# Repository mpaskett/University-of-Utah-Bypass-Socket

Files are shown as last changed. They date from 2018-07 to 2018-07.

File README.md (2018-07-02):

# University-of-Utah-Bypass-Socket
The University of Utah’s bypass socket is a powerful tool enabling non-amputees to perform functional tasks with upper-limb prosthetic devices. Utilizing modular 3D-printed components, the bypass socket can be easily adapted to virtually any prosthetic device. We hope the bypass socket can become a useful resource to researchers, clinicians, educators, and insurers in the upper-limb prosthetics field. 

Find the necessary instructions and files for making your own bypass socket here.

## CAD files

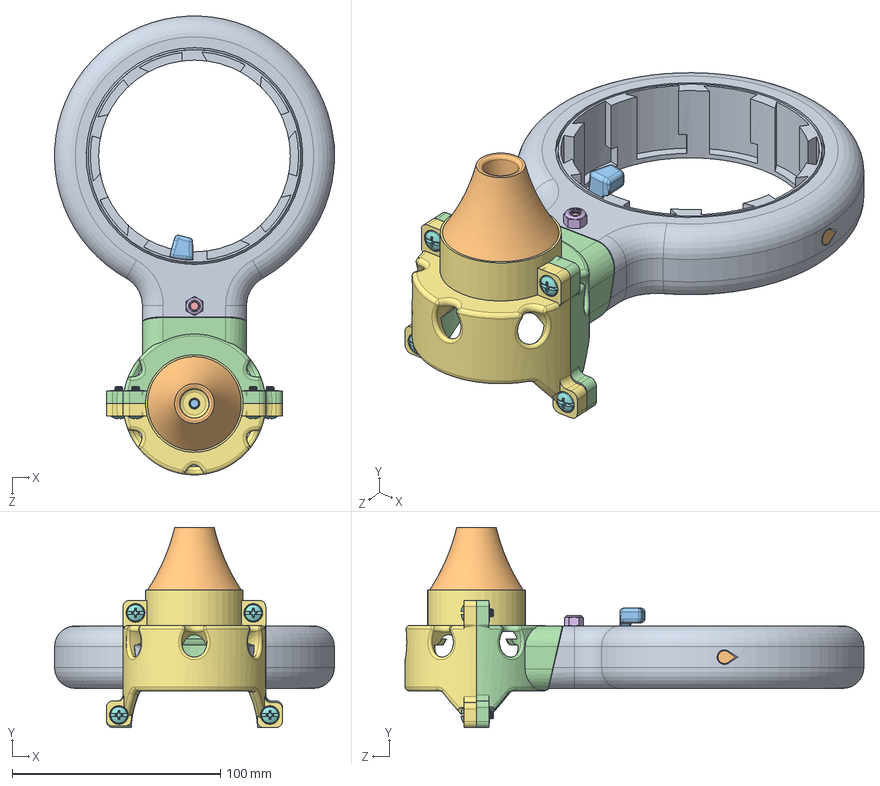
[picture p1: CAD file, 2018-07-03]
Assemblies/Wrist Assembly.SLDASM
134.4 x 96.0 x 220.2 mm
Bypass Bearing Keyfit
Bypass Bearing Insert
Wrist Locker
DEKA Bypass Adapter Nut Side
M5 Hex Screw Wrist - 91280A238
Nylon Insert Locknut - 90576A104
DEKA Bypass Adapter Bolt Side
8-32 Phillips Screw Wrist - 90604A194 x 4
8-32 Steel Hex Nut Wrist - 90480A009 x 4
Bypass Adapter Proximal Support
M5 Hex Head Screw Wrist - 91280A242

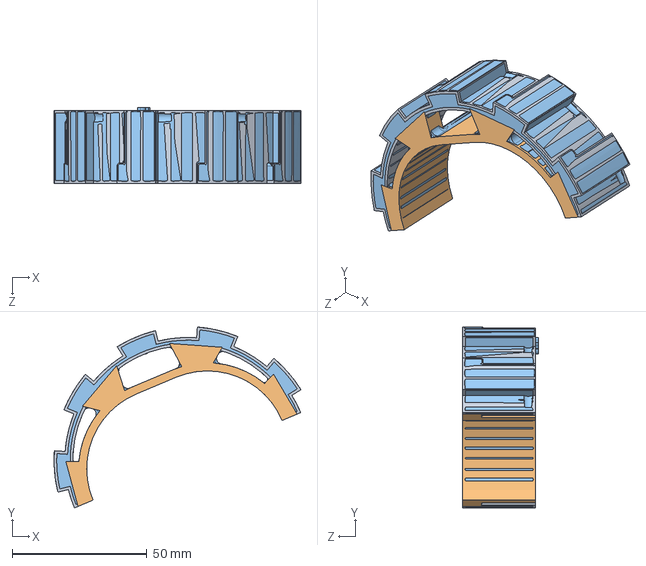
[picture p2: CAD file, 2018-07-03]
Parts/3D Prints/Normal Support/Wrist Attachment Small.SLDASM
91.5 x 67.0 x 28.0 mm

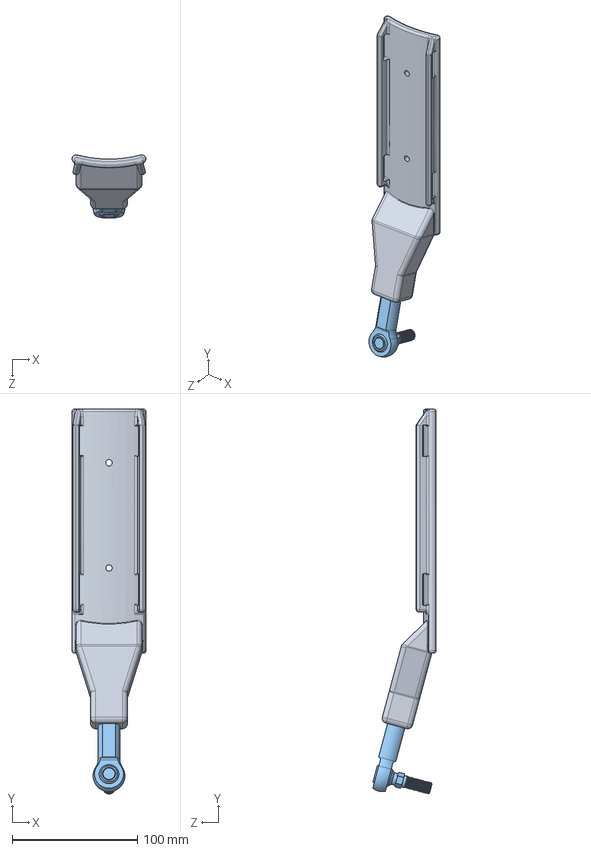
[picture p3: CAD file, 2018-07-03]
Assemblies/Humeral Attachment Assembly.SLDASM
59.0 x 307.5 x 50.6 mm
Humeral Attachment
3_8-16 Hex Nut 90473A031
Ball Joint 60745K841
Thread Adapter

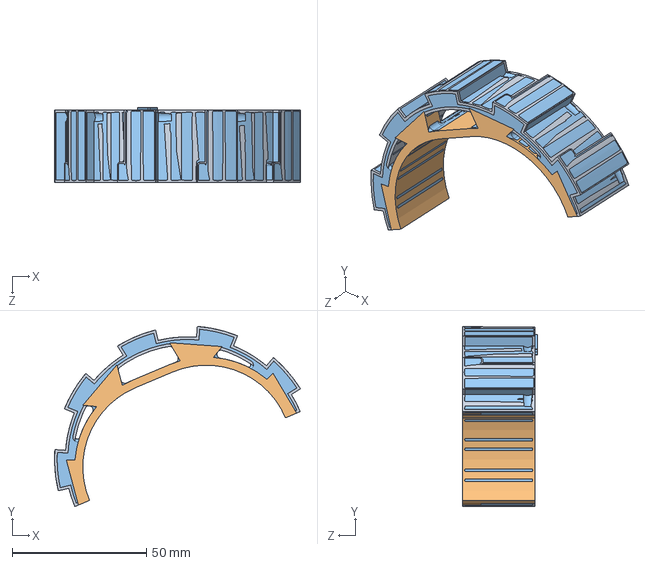
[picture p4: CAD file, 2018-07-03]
Parts/3D Prints/Normal Support/Wrist Attachment Medium.SLDASM
91.5 x 67.0 x 28.0 mm

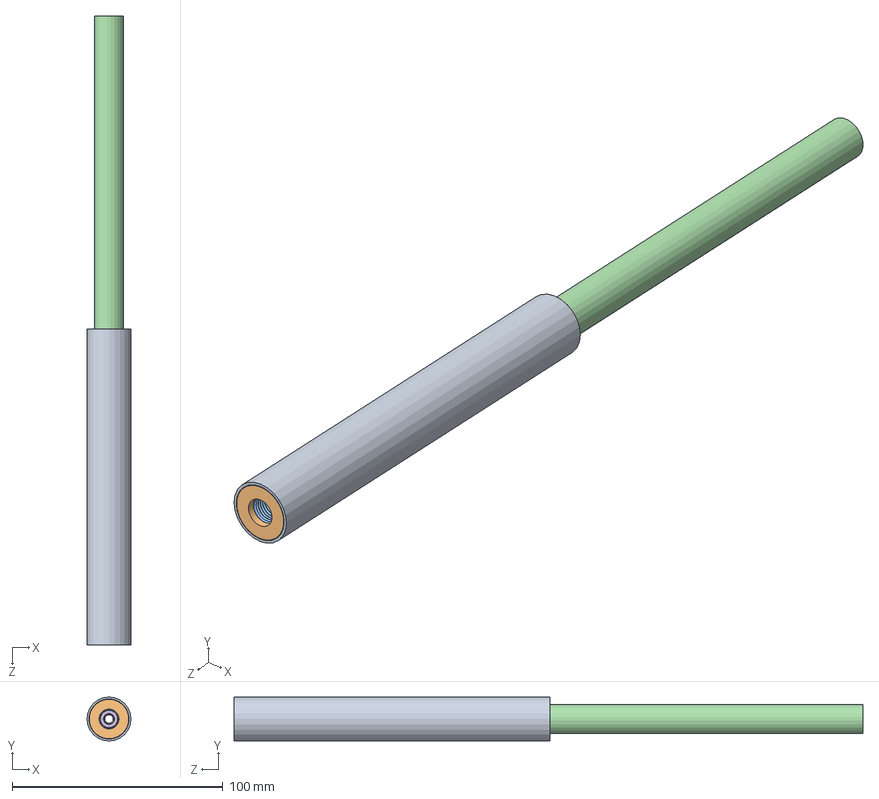
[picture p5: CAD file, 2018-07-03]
Assemblies/Telescoping System Assembly.SLDASM
20.9 x 20.9 x 298.8 mm
CF Rod Large
CF Insert - Large - Elbow End
3_8-24 Hex Nut 90473A215 x 2
CF Rod Small
CF Slider - Inner x 2
CF Insert - Small - Wrist End
M5 Hex Nut - 90591A146 x 2

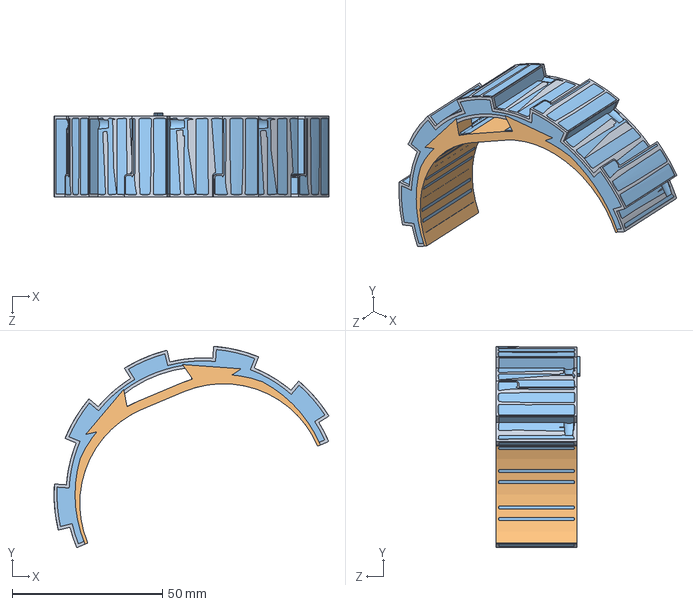
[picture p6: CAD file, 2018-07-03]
Parts/3D Prints/Normal Support/Wrist Attachment Large.SLDASM
91.5 x 67.0 x 28.0 mm

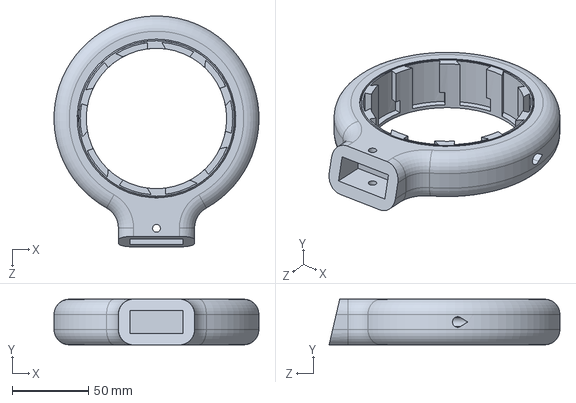
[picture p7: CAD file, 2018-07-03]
Parts/3D Prints/Dissolvable Support/Bypass Bearing Keyfit.SLDPRT
134.4 x 30.0 x 151.3 mm

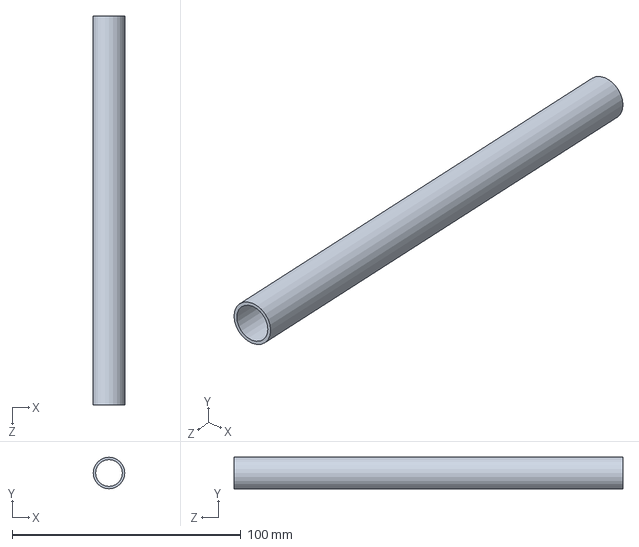
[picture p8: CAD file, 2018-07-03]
Parts/Hardware/CF Rod Small.SLDPRT
13.8 x 13.8 x 170.0 mm

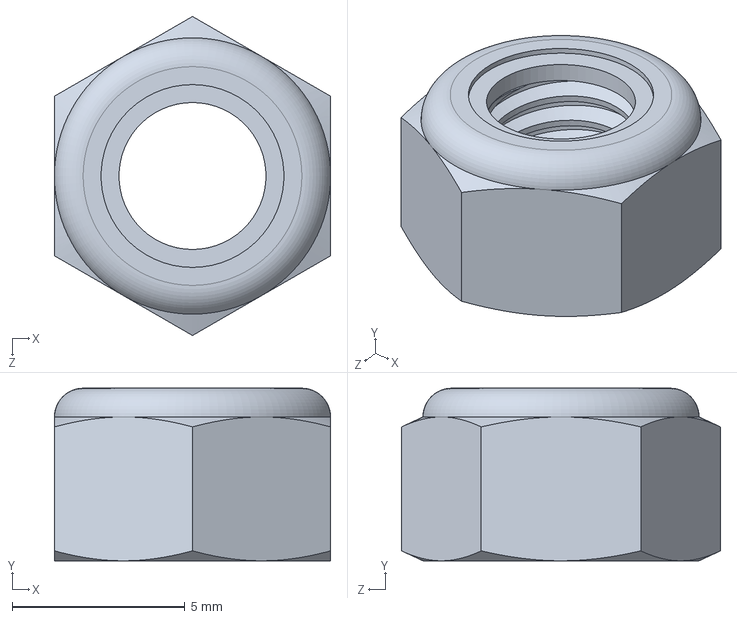
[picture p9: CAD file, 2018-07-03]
Parts/Hardware/Nylon Insert Locknut - 90576A104.SLDPRT
8.00 x 5.00 x 9.24 mm

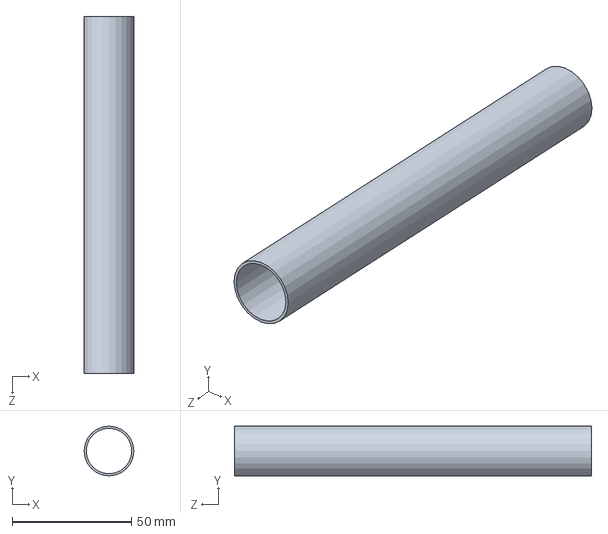
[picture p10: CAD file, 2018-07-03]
Parts/Hardware/CF Rod Large.SLDPRT
20.9 x 20.9 x 150.0 mm

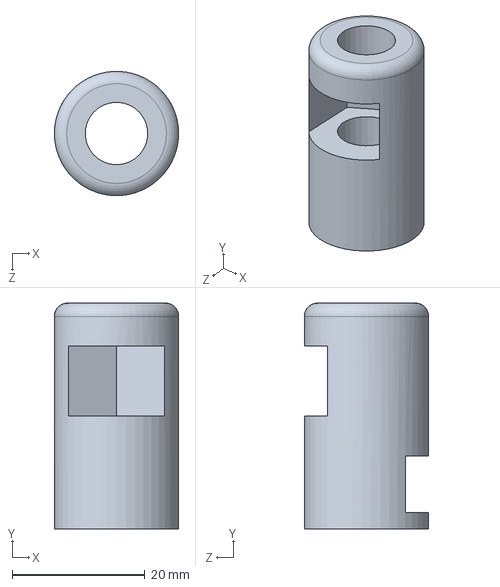
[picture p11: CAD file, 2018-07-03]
Parts/3D Prints/Normal Support/CF Insert - Large - Elbow End.SLDPRT
18.7 x 34.0 x 18.7 mm

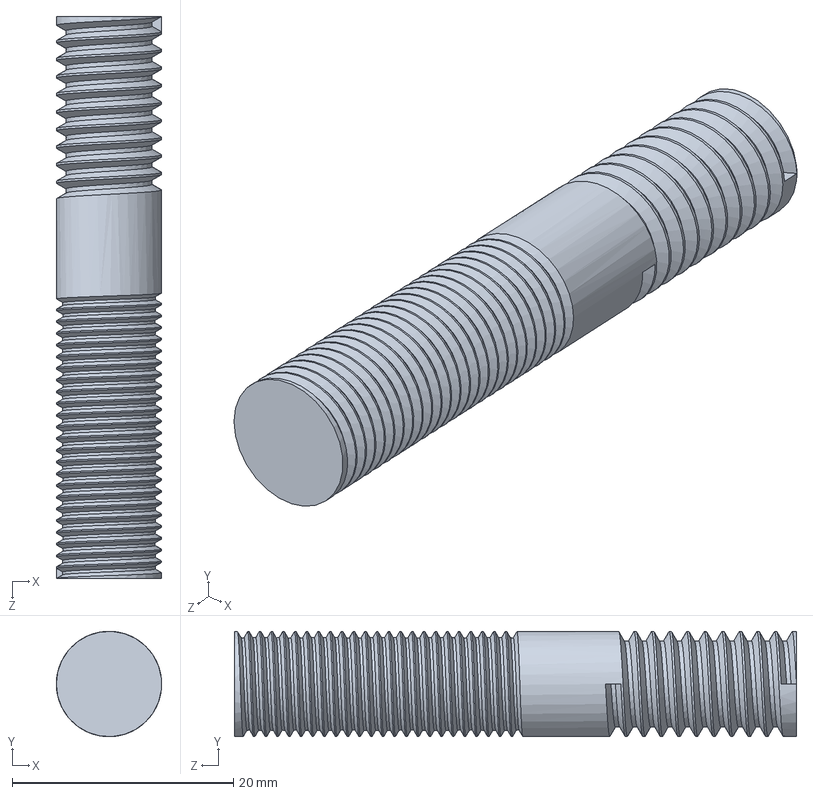
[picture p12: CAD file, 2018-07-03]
Parts/Hardware/Thread Adapter.SLDPRT
9.53 x 9.52 x 50.8 mm

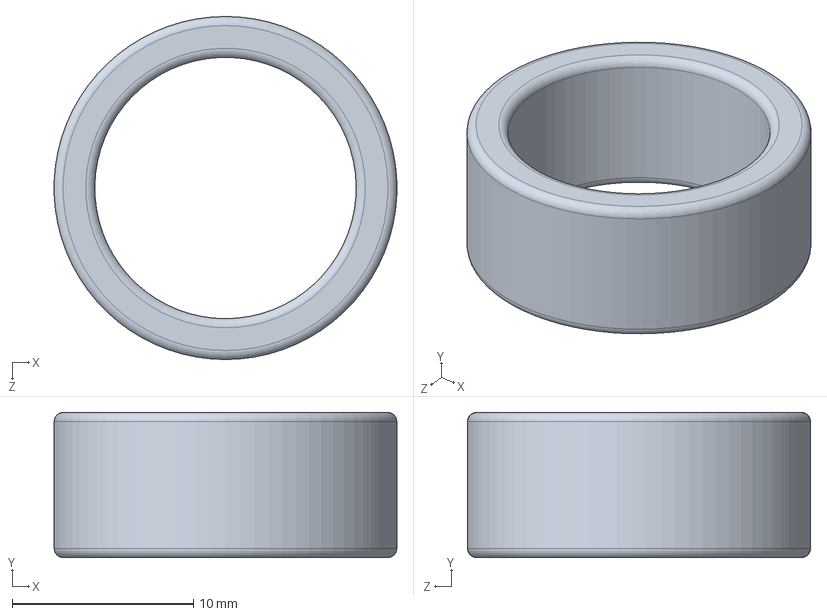
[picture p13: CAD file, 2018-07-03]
Parts/3D Prints/Normal Support/CF Slider - Outer.SLDPRT
18.9 x 8.00 x 18.9 mm

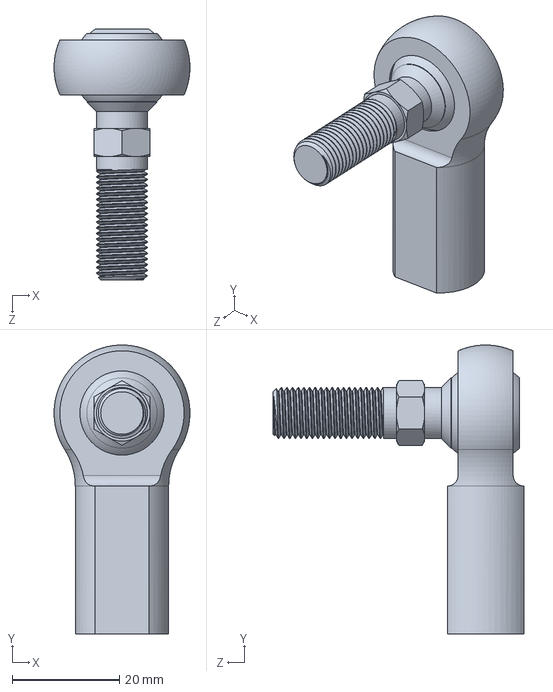
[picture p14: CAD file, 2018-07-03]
Parts/Hardware/Ball Joint 60745K841.SLDPRT
25.4 x 54.0 x 46.8 mm

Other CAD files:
Parts/3D Prints/Normal Support/Humeral Attachment.SLDPRT
Parts/3D Prints/Normal Support/Bypass Bearing Drill Attachment.SLDPRT
Parts/3D Prints/Normal Support/Wrist Locker.SLDPRT
Parts/3D Prints/Normal Support/Bypass Adapter Proximal Support.SLDPRT
Parts/3D Prints/Dissolvable Support/Bypass Bearing Keyfit.STL
Parts/3D Prints/Normal Support/Bypass Bearing Insert.SLDPRT
Parts/3D Prints/Normal Support/CF Insert - Small - Wrist End.SLDPRT
Parts/3D Prints/Normal Support/CF Slider - Inner.SLDPRT
Parts/3D Prints/Normal Support/CF Slider.SLDPRT
Parts/3D Prints/Normal Support/DEKA Bypass Adapter Bolt Side.SLDPRT
Parts/3D Prints/Normal Support/DEKA Bypass Adapter Nut Side.SLDPRT
Parts/3D Prints/Normal Support/Quick-Disconnect Bolt Side.SLDPRT
Parts/3D Prints/Normal Support/Quick-Disconnect Nut Side.SLDPRT
Parts/3D Prints/Normal Support/STL/Bypass Adapter Proximal Support.STL
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

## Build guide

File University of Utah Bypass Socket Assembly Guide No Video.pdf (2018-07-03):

# The University of Utah Bypass Socket

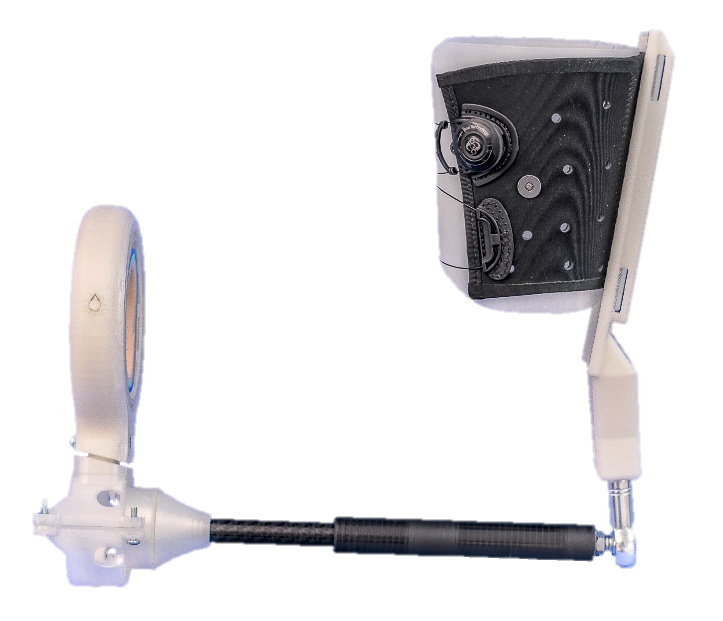
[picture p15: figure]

# Enabling Researchers to Perform Real-World Tasks with Prosthetic Devices

# Michael Paskett

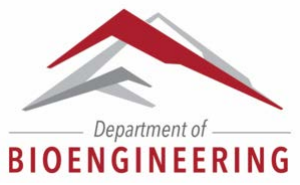
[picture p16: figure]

## Table of Contents

Introduction | 3
Materials | 3
3D-Printed Parts | 3
Commercial Parts | 4
Tools | 5
Assembly | 5
Humeral Attachment Assembly | 5
Parts: | 5
Assembly: | 5
Boa® Enclosure Variation | 8
Telescoping System | 9
Parts: | 9
Preparing the carbon fiber rods: | 9
Assembly: | 10
Wrist Attachment Assembly | 13
Parts: | 13
Bypass Bearing Preparation: | 13
Wrist Attachment Preparation: | 14
Assembly: | 15
Final Assembly | 18

Introduction The University of Utah’s bypass socket is a powerful tool enabling non-amputees to perform functional

tasks with upper-limb prosthetic devices. Utilizing modular 3D-printed components, the bypass socket can be easily adapted to virtually any prosthetic device. We hope the bypass socket can become a useful resource to researchers, clinicians, educators, and insurers in the upper-limb prosthetics field.

Materials The bypass socket is comprised of 3D-printed parts and commercially-available components.

3D-Printed Parts
The 3D-printed parts are all available online. With the exception of the Bypass Bearing, all parts are printed with ABS (we used a Fusion3 F400 printer). The Bypass Bearing was printed with dissolvable PVA support on an Ultimaker 3.
The assembly is divided into 3 sections; the 3D-printed parts necessary for each sub-assembly are listed below:
- Humeral Attachment Assembly
- Humeral Attachment
- Telescoping System Assembly
- CF Insert – Large – Elbow End
- 2x - CF Slider – Inner
- CF Insert – Small – Wrist End
- Wrist Assembly
- Bypass Bearing Keyfit
- Bypass Bearing Insert
- 6x - Wrist Attachments
- 2x - Small
- 2x - Medium
- 2x - Large
- Wrist Locker
- 4x - Terminal Device Adapters
- DEKA Bypass Adapter Nut Side
- DEKA Bypass Adapter Bolt Side
- Quick-Disconnect Bolt Side
- Quick-Disconnect Nut Side
- Bypass Adapter Proximal Support

Commercial Parts
Please note that most of these parts can be found at a local hardware store, which will reduce costs associated with buying materials in bulk from vendors such as McMaster-Carr.
Item | Quantity | Link | Assembly
3/8”-16 Hex Nut | 1 | https://www.mcmaster.com/#90473a031/=1d6pd4a | Humeral
Ball Joint | 1 | https://www.mcmaster.com/#60745k841/=1d6pdhe | Humeral
Thread Adapter | 1 | https://www.mcmaster.com/#94358a330/=1d6pe53 | Humeral
½” Carbon Fiber Rod | 1 | https://www.rockwestcomposites.com/45240-group | Telescoping
¾” Carbon Fiber Rod | 1 | https://www.rockwestcomposites.com/45035 | Telescoping
3/8”-24 Hex Nut | 2 | https://www.mcmaster.com/#90473a215/=1d6pj34 | Telescoping
M5 Hex Nut | 2 | https://www.mcmaster.com/#90591a146/=1d6pjki | Telescoping
30 mm M5 Hex Screw | 1 | https://www.mcmaster.com/#91280a238/=1d6pk30 | Wrist
M5 Nylon Insert Locknut | 1 | https://www.mcmaster.com/#90576a104/=1d6pkot | Wrist
8-32 ½” Phillips Slotted Screw | 4 | https://www.mcmaster.com/#90604a194/=1d6pkvt | Wrist
8-32 Hex Nut | 4 | https://www.mcmaster.com/#90480a009/=1d6pldg | Wrist
40 mm M5 Hex Head Screw | 1 | https://www.mcmaster.com/#91280a242/=1d6plt5 | Wrist
18” x 1” Velcro Straps | 1 | https://www.amazon.com/VELCRO-Brand-90107-Purpose-Straps/dp/B000TGX0HK | Humeral Attachment
2-Part Epoxy | 1 | https://www.amazon.com/J-B-Weld-8276-KwikWeld-Reinforced/dp/B0006O1ICY | Telescoping
Foam – TRLM-00009 Puf+SRP+Puf | 1 | https://store.acor.com/products/Multi-Laminated-Materials-by-Acor.html | Wrist
6 mm Airsoft BBs | 1 | https://www.amazon.com/Soft-Air-Bottle-Ultrasonic-Airsoft/dp/B0013CJKXM | Wrist
Super Glue | 1 | https://www.amazon.com/Scotch-Super-Liquid-Ounces-AD114/dp/B001PILFVY | Wrist
Wax-Based Chain Lube | 1 | https://www.amazon.com/Pedros-Ice-Wax-2-0-Bottle/dp/B002VLK15K | Wrist

Tools
- Dremel with diamond cutting blade
- Electric drill
- Phillips screwdriver
- 120-grit sandpaper

## Assembly

Humeral Attachment Assembly
Parts:
- 3D Printed
- Humeral Attachment
- Hardware
- 3/8”-16 Hex Nut
- Ball Joint
- Thread Adapter
Assembly:
1. Insert the 3/8”-16 hex nut into the slot on the Humeral Attachment
2. Attach the thread adapter through the Humeral Attachment hole
3. Attach the ball joint

Video:

Figure 1 - Humeral Attachment Assembly Video

3D Model:

Figure 2 - Humeral Attachment Assembly 3D Model

Exploded view:

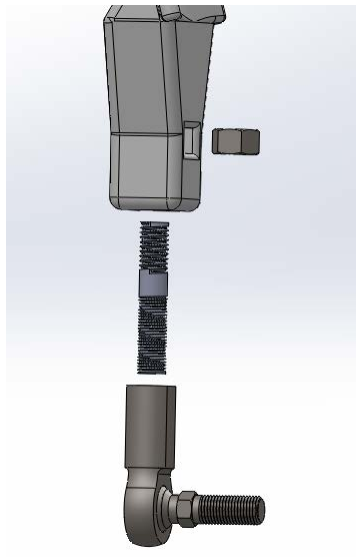
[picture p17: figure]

Figure 3 - Humeral Attachment Exploded Assembly
Notes:
- The ball joint will likely still be able to rotate even when flush with the bottom of the Humeral Attachment. This allows greater range of motion when the bypass socket is completely assembled.
- The PTFE liner on the ball joint may require a break-in to move more freely. We attached the joint to a drill and rotated at high velocity while using household oil to reduce heat/damage to the ball joint.

Boa® Enclosure Variation
We contracted with a local prosthetics company (Peak Prosthetics, Salt Lake City, UT) to attach a Boa® enclosure system. This has greatly reduced fatigue experienced when operating the bypass socket with a heavier terminal device (e.g., DEKA LUKE arm - 1.5 kg, 3.3 lbs). A similar product may be found here: https://www.clickmedical.co/store/orthofit/orthofit-lacers/. The inner component of the sleeve is a high-density polyethylene sheet. Feel free to contact Peak Prosthetics if you desire a similar configuration.

The Boa® enclosure system is shown here:

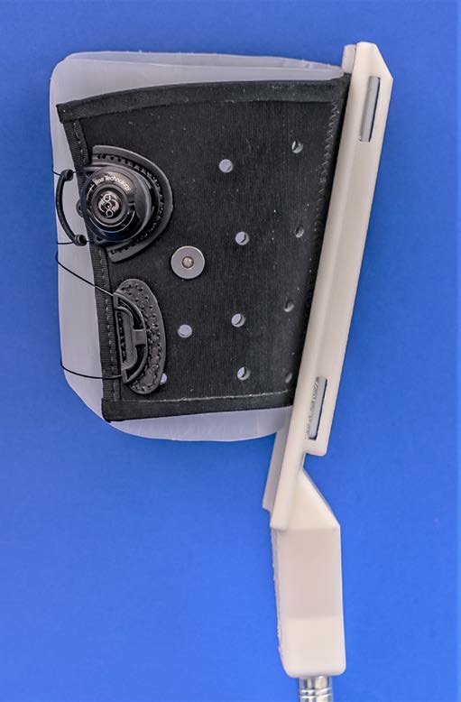
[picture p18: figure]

Figure 4 – Boa® Enclosure System on Humeral Attachment
Telescoping System
Parts:
- 3/4” Carbon Fiber Rod
- CF Insert – Large – Elbow End
- 2x 3/8”-24 Hex Nut
- 1/2” Carbon Fiber Rod
- 2x CF Slider – Inner
- CF Insert – Small – Wrist End
- 2x M5 Hex Nut
Preparing the carbon fiber rods:
Cut the ¾” carbon fiber rod to 150 mm, and the ½” carbon fiber rod to 170 mm. We used a Dremel with a diamond blade to cut the carbon fiber. The dust from carbon fiber is toxic. Work in a well-ventilated area with proper PPE.

Assembly:
In this assembly, we recommend dry-setting the different components before applying any epoxy, as any errors will likely require the assembly to be redone.
1. Insert the M5 hex nuts into the “CF Insert – Small – Wrist End”
2. Epoxy the “CF Insert – Small – Wrist End” to the inside of the 1/2” carbon fiber rod
a. Apply a coat of epoxy around the outside of the “CF Insert – Small – Wrist End” and insert it into the carbon fiber rod. Be careful not to epoxy the hex nuts.
b. Remove excess epoxy
3. Epoxy the “CF Slider – Inner” to the opposite end of the 1/2” carbon fiber rod
a. Apply a coat of epoxy on the outside of the carbon fiber rod and insert it onto the “CF Slider – Inner”
b. Remove excess epoxy
4. Epoxy another “CF Slider – Inner” to the inside of the large carbon fiber rod
a. Apply a coat of epoxy on the outside of the “CF Slider – Inner” and insert into the 3/4” carbon fiber rod
b. Remove excess epoxy
5. Insert the 1/2” carbon fiber rod through the 3/4” carbon fiber rod such that the hex nuts are on the distal end
a. Note: this must be aligned correctly for the telescoping system to function
6. Insert the 3/8”-24 hex nuts into the “CF Insert – Large – Elbow End”
7. Epoxy the “CF Insert – Large - Elbow End” to the inside of the 3/4” carbon fiber rod
a. Apply a coat of epoxy around the outside of the “CF Insert – Small – Wrist End” and insert it into the carbon fiber rod. Be careful not to epoxy the hex nuts.
b. Remove excess epoxy

Video:

Figure 5 - Telescoping System Assembly Video

3D Model:

Figure 6 - Telescoping System 3D Model

Exploded view:

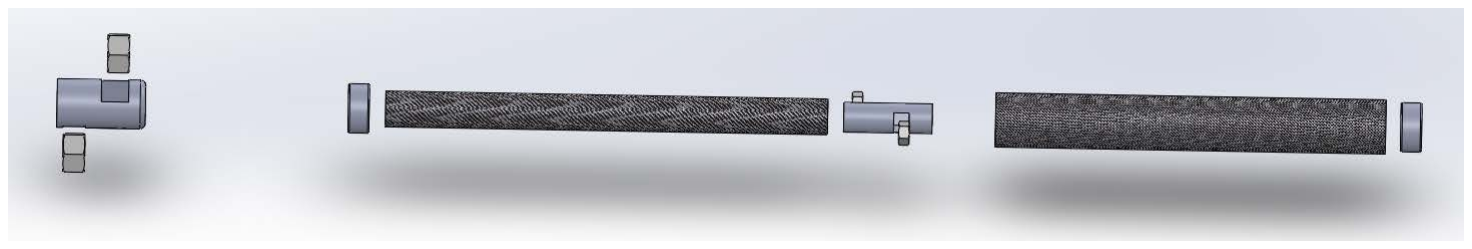
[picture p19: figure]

Figure 7 - Exploded View of Telescoping System
Section view:

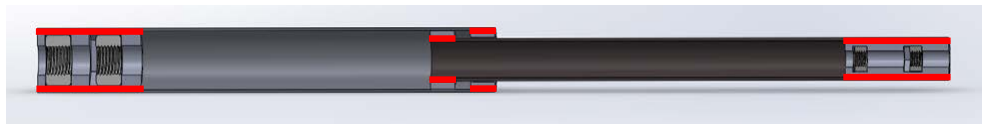
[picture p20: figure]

Figure 8 - Section View of Telescoping System. Red indicates epoxied pieces.
Wrist Attachment Assembly
Parts:
- Bypass Bearing Keyfit
- Bypass Bearing Insert
- 2x Wrist Attachment
- Wrist Locker
- 2x Terminal Device Adapter
- In this example:
- DEKA Bypass Adapter Nut Side
- DEKA Bypass Adapter Bolt Side
- M5 Hex Screw Wrist
- Nylon Insert Locknut
- 4x 8-32 Phillips Screw Wrist
- 4x 8-32 Steel Hex Nut Wrist
- Bypass Adapter Proximal Support
- M5 Hex Head Screw Wrist
- Bypass Bearing Drill Attachment
- Tri-density Foam
Bypass Bearing Preparation:
The “Bypass Bearing Keyfit” must be printed with dissolvable support. We printed with an Ultimaker 3, using PLA and PVA (dissolvable in water). We soaked the print overnight and removed what support material we could with small tools. After removing the majority of support material to the extent that the internal part of the bearing can rotate freely, move on to breaking in the bearing.
The bypass bearing requires a break-in to reduce friction. After dissolving the support material in the “Bypass Bearing Keyfit,” insert enough 6 mm airsoft BBs to fill 2/3 of the internal track (~40 BBs). Temporarily tape the hole shut. Liberally apply a wax-based bike chain lube along the rim of the “Bypass

Bearing Keyfit,” and using an electric drill, spin the lube into the bearings. After spinning through with chain lube, submerge the “Bypass Bearing Keyfit” in water and spin again to remove any particulate and excess wax in the internal track. Repeat this process until the bearings move with very little friction. We ended up attaching a ½” threaded rod to the underside of the “Bypass Bearing Drill Attachment” which provided much greater torque and stability when using the drill. This break-in process may require several iterations – the bearings need plenty of wiggle room. When the bearings are sufficiently smooth, apply chain lube again and let dry. Finally, remove the tape and epoxy the “Bypass Bearing Insert” into the “Bypass Bearing Keyfit.”

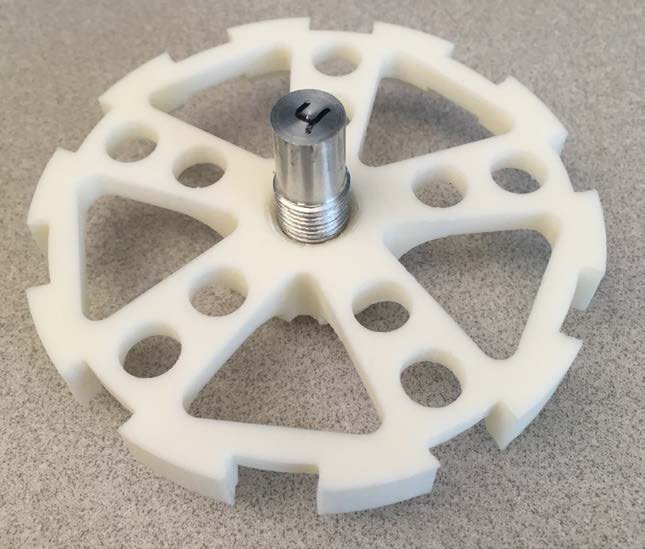
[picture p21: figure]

Figure 9 - 1/2" Threaded Rod on “Bypass Bearing Drill Attachment”
Wrist Attachment Preparation:
We applied tri-density foam on the interior of the wrist attachments to increase comfort, especially when using heavier terminal devices. We used superglue to adhere the foam to the plastic.

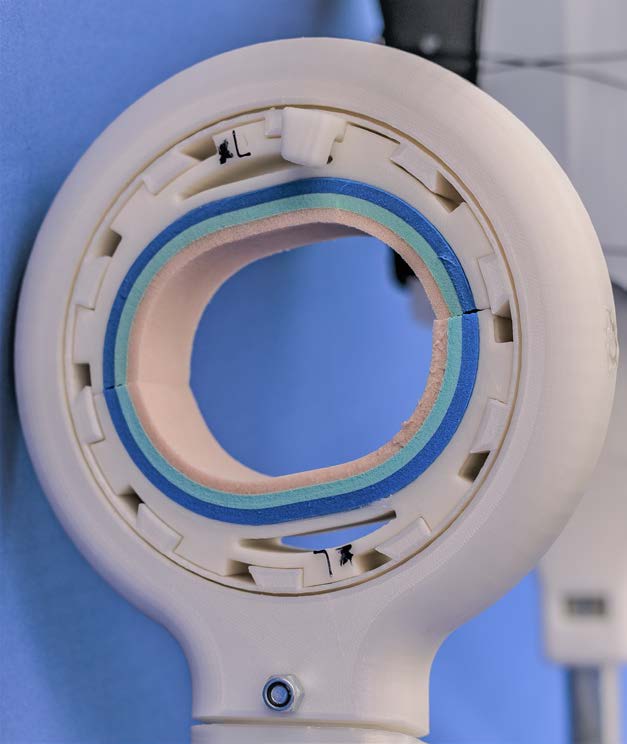
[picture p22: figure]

Figure 10 - Tri-Density Foam on Wrist Attachment
Assembly:
1. Epoxy “Bypass Adapter Proximal Support” to “Terminal Device Adapter”
2. Insert M5 Hex Screw Wrist into “DEKA Bypass Adapter Bolt Side” (Terminal Device Adapter)
3. Insert four 8-32 hex nuts into “DEKA Bypass Adapter Nut Side” (Terminal Device Adapter)
a. These nuts may be epoxied in for ease
4. Insert terminal device
5. Join “DEKA Bypass Adapter Nut Side” with “DEKA Bypass Adapter Bolt Side” around terminal device
6. Fasten four 8-32 Philips screws to secure terminal device
7. Insert “DEKA Bypass Adapter Nut Side” into “Bypass Bearing”
8. Insert M5 hex screw into “Bypass Bearing”
9. Fasten M5 nylon insert locknut onto “Bypass Bearing”
10. Insert “Wrist Attachments” and rotate
11. Insert “Wrist Locker”

Video:

Figure 11 - Wrist Attachment Assembly Video

3D Model:

Figure 12 - Wrist Attachment 3D Model

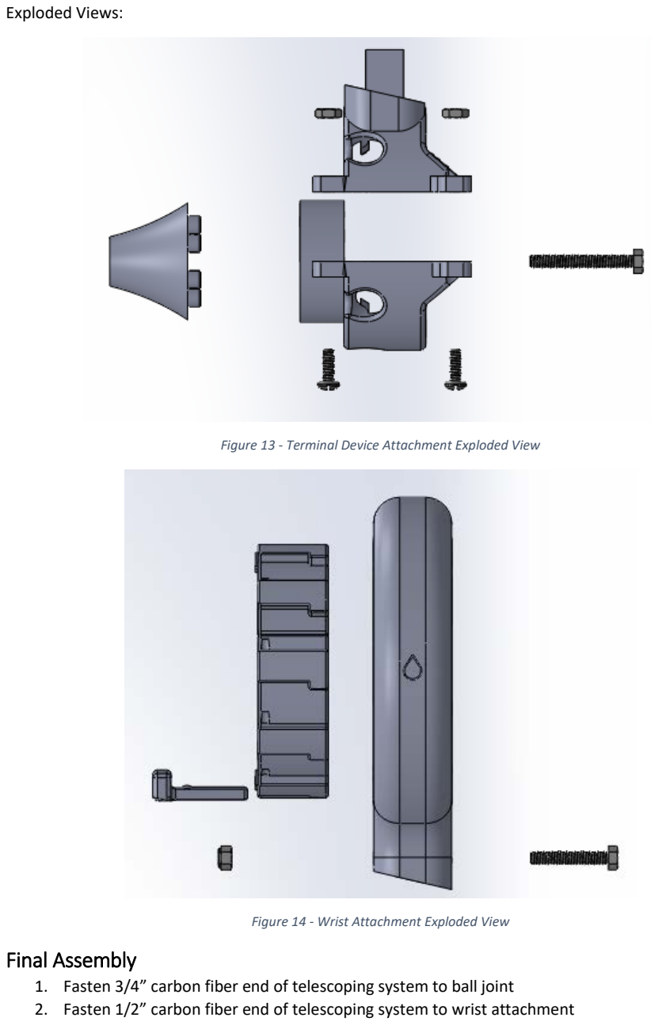
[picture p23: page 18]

Exploded Views:

Figure 13 - Terminal Device Attachment Exploded View

Figure 14 - Wrist Attachment Exploded View
Final Assembly
1. Fasten 3/4” carbon fiber end of telescoping system to ball joint
2. Fasten 1/2” carbon fiber end of telescoping system to wrist attachment

Video:

Figure 15 - Final Assembly Video

3D Model:

Figure 16 - Final Assembly 3D Model

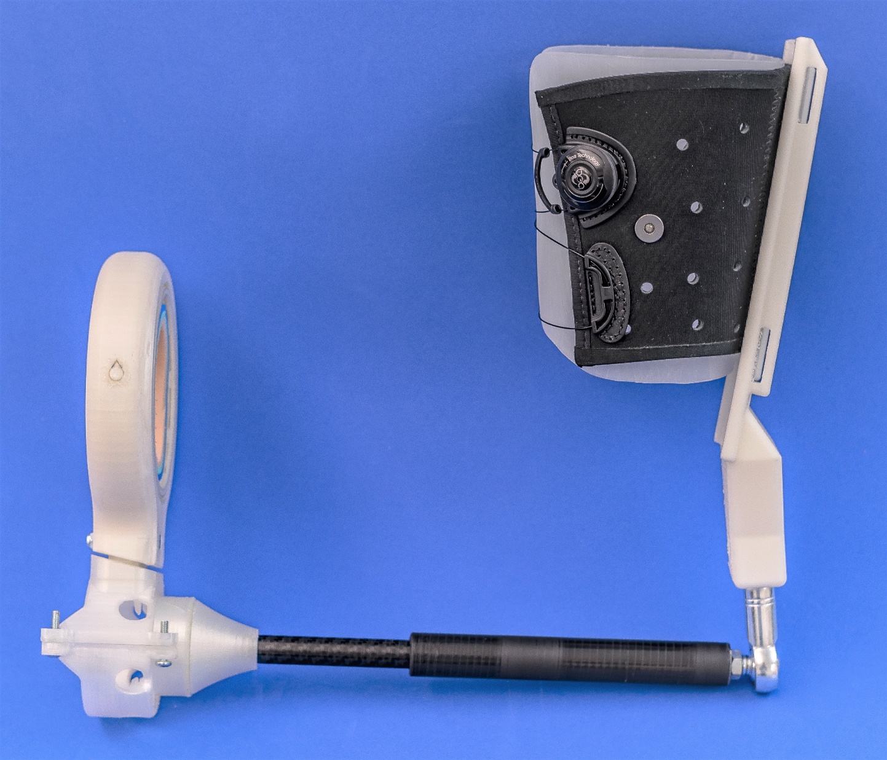
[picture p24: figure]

Figure 17 - Completed Bypass Socket
Congratulations! Your bypass socket is complete!
